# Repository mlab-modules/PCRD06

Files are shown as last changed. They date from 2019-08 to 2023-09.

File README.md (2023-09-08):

<!--- PrjInfo ---> <!--- Please remove this line after manually editing --->
<!--- 00a56be08b96043df9e37d6aff7b6990 --->
<!--- Created:2019-08-04 12:46:39.528455: --->
<!--- Author:: --->
<!--- AuthorEmail:: --->
<!--- Tags:: --->
<!--- Ust:: --->
<!--- Label --->
<!--- ELabel --->
<!--- Name:PCRD06A: --->
# PCRD06A Sample and hold circuit with analog memory
<!--- LongName --->
Signal follower with analog memory. It is a circuit equivalent to a sample-hold circuit triggered by a falling edge of signal or a circuit equivalent to a peak detector. The PCRD06A module is normally used in combination with SiPM based scintillation detector.

Examples of detectors that could be connected to the PCRD analog-backend.

  * [SIMP02](https://github.com/mlab-modules/SIPM02)
  * [USTSIPM01](https://github.com/ust-modules/USTSIPM01)

<!--- ELongName --->

<!--- Lead --->

<!--- ELead --->

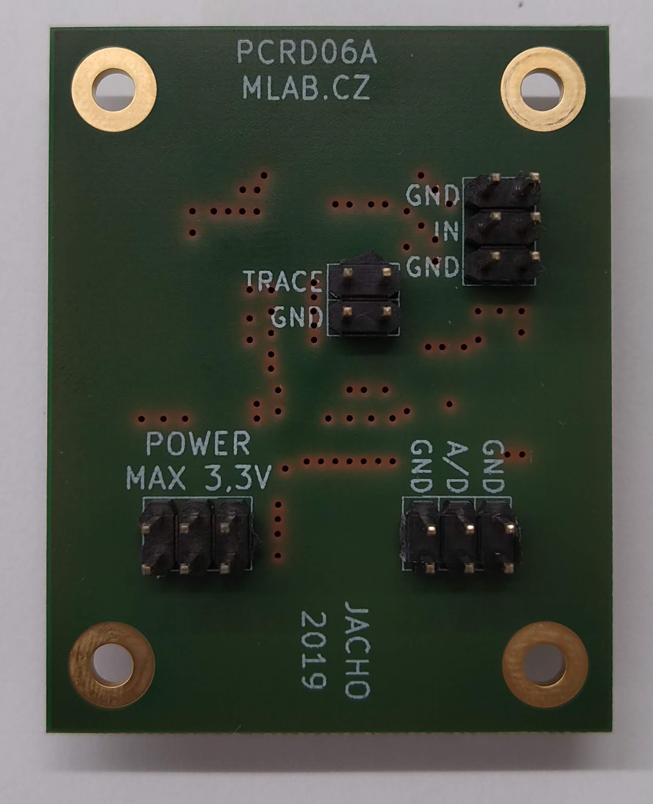
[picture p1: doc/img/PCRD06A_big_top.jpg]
PCRD06A


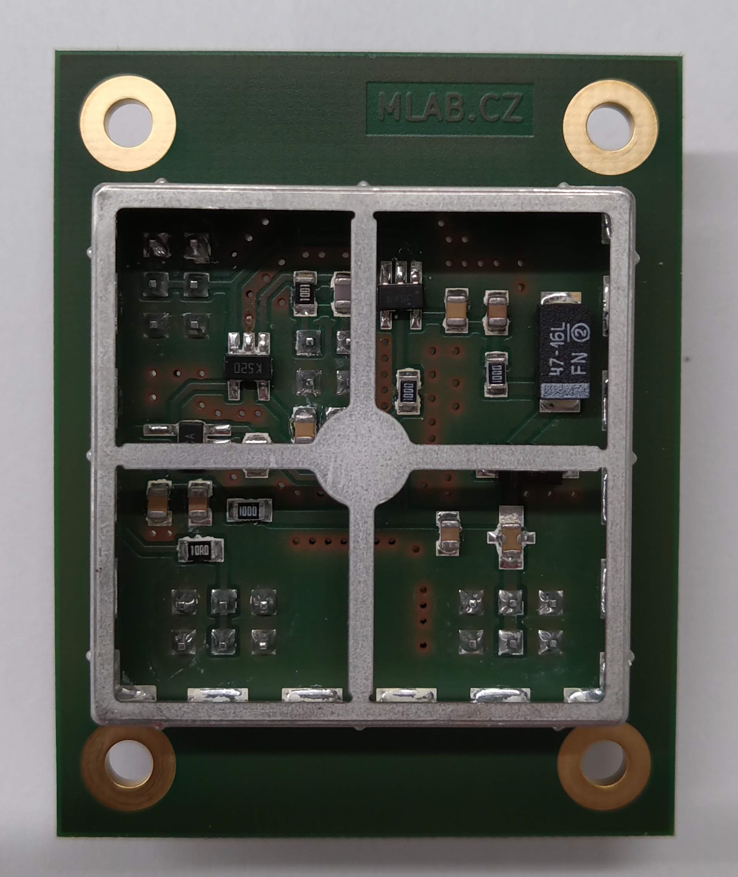
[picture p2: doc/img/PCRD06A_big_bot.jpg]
PCRD06A


<!--- Description --->

### Basic usage 

The circuit is able to operate in multiple modes. The operation mode depends on the logic used to control the circuit.  

  1. The first operation mode is the peak detector, which stores the maximal value of peak output from SiPM. This mode holds the maximal value of pulse until the circuit is reset (usually after AD conversion)
  2. Pulse discriminator, where the AD converted value is compared with a predefined threshold. After passing this threshold the circuit should be reset. 
  3. The energy integrator in that mode signal is ADconverted as fast as possible, and the dose is integrated numerically over the specified time interval. 

### Principle of function 

The signal output from the scintillation detector is a pulse. The pulses are stored in a specially developed sample-hold circuit that behaves as a signal follower and analog memory. When signal #PeakDetect_Trace is in H an analog switch U5 turns on and a signal at an output U2 follows a signal at the input with a slight delay which is done by R13 and C19. If signal #PeakDetect_Trace is switched to a high impedance state the analog switch U5 starts to be controlled by a comparator U1. In this case, when the input signal goes from high to low, a positive input of the comparator will be at a higher voltage than a negative input, following a voltage at capacitor C19.

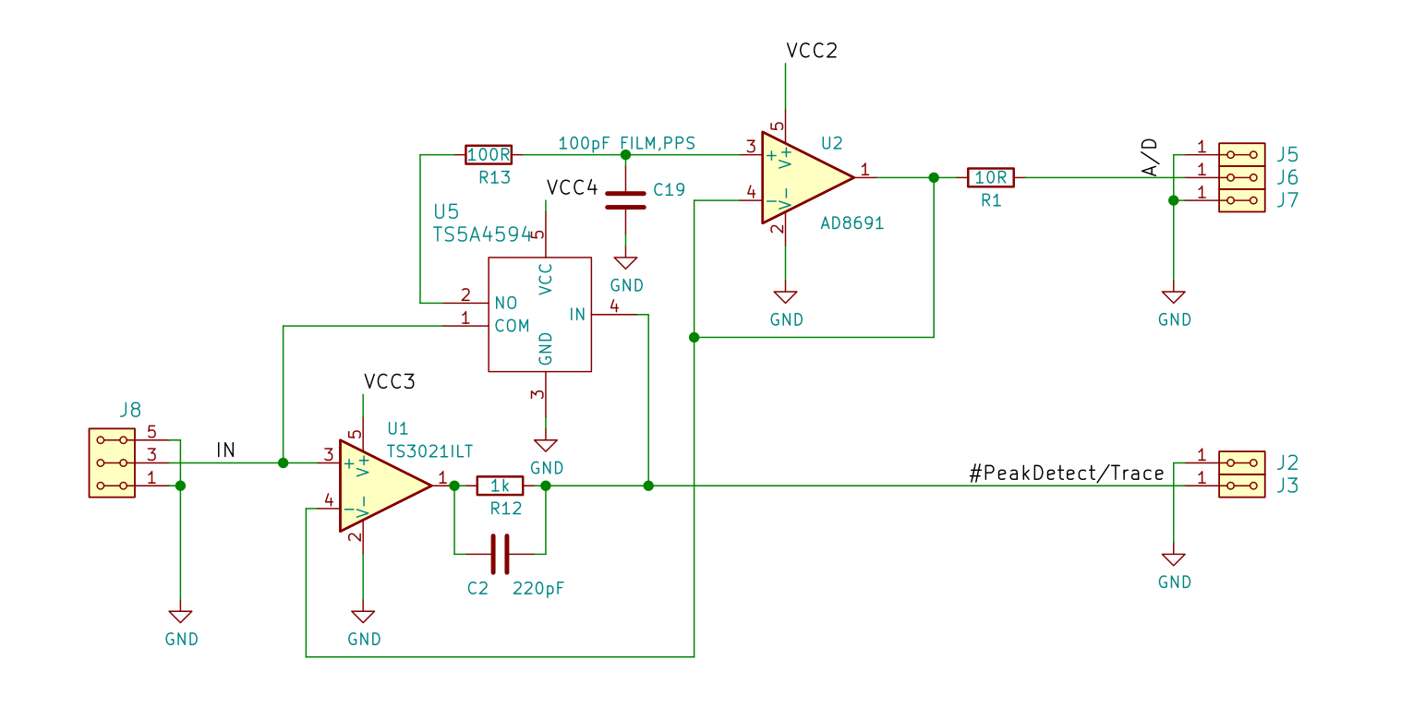
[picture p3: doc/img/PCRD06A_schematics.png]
PCRD06A


It causes the switching-off of the analog switch U5 and the capacitor C19 holds its last voltage value. This behavior is similar to a peak detector circuit. In the next step, the stored voltage can be converted by ADC connected at the output and after this conversion, the input #PeakDetect_Trace goes again to H and the circuit changes behavior to signal follower circuit. The described sample-hold circuit does not suffer from typical peak detector circuit ills like insensitivity to small signals, mistreatment of negative signals, or discharging the capacitor by leakage current through diodes.

Moreover, this circuit can be used as a pulse discriminator as well. The signal #PeakDetect_Trace can be connected to an input of digital circuits when it is controlled by the comparator U1. When the input signal goes from high to low, the signal #PeakDetect_Trace goes from high to low as well. This behavior can be used for the detection of the falling edge of the signal. There is only one constraint of this circuit, the input signal can not change raising/falling time widely and the RC time constant (R13, C19) must be chosen correctly, respecting the input signal time properties.

More details about the principle are in [DOCTORAL THESIS, Research on cosmic rays on board aircraft using a newly developed PIN diode detector, 2020, CTU in Prague](http://www.ujf.cas.cz/export/sites/ujf/.content/files/CRREAT/kakona_thesis.pdf)

<!--- EDescription --->
<!--- Content --->
<!--- EContent --->
<sub><sup> Generated with [MLABweb](https://github.com/MLAB-project/MLABweb). (2019-08-04)</sup></sub>

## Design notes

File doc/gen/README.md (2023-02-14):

# PCB

Board size: 50.29x40.13 mm (1.98x1.58 inches)

- This is the size of the rectangle that contains the board
- Thickness: 1.6 mm (63 mils)
- Material: FR4
- Finish: HAL
- Layers: 2
- Copper thickness: 35 µm

Solder mask: TOP / BOTTOM

- Color: Green

Silk screen: TOP / BOTTOM

- Color: White

# Important sizes

Clearance: 0.2 mm (8 mils)

Track width: 0.25 mm (10 mils)

- By design rules: 0.2 mm (8 mils)

Drill: 0.5 mm (20 mils)

- Vias: 0.5 mm (20 mils) [Design: 0.4 mm (16 mils)]
- Pads: 1.0 mm (39 mils)
- The above values are real drill sizes, they add 0.1 mm (4 mils) to plated holes (PTH)

Via: 0.8/0.4 mm (31/16 mils)

- By design rules: 0.8/0.3 mm (31/12 mils)
- Micro via: no [0.2/0.1 mm (8/4 mils)]
- Burried/blind via: no

Outer Annular Ring: 0.15 mm (6 mils)

- By design rules: 0.15 mm (6 mils)

Eurocircuits class: 4B
- Using min drill 0.5 mm for an OAR of 0.15 mm

# General stats

Components count: (SMD/THT)

- Top: 0/11 (THT)
- Bottom: 21/1 (SMD + THT)

Defined tracks:

- 0.25 mm (10 mils)
- 0.3 mm (12 mils)
- 0.4 mm (16 mils)
- 0.5 mm (20 mils)
- 0.6 mm (24 mils)
- 0.7 mm (28 mils)
- 0.8 mm (31 mils)

Used tracks:

- 0.25 mm (10 mils) (6) defined: yes
- 0.4 mm (16 mils) (68) defined: yes
- 0.8 mm (31 mils) (17) defined: yes

Defined vias:

- 0.8/0.4 mm (31/16 mils)

Used vias:

- 0.8/0.4 mm (31/16 mils) (Count: 72, Aspect: 2.0 A) defined: yes

Holes (excluding vias):

- 0.89 mm (35 mils) (22)
- 3.0 mm (118 mils) (4)

Oval holes:

Drill tools (including vias and computing adjusts and rounding):

- 0.5 mm (20 mils) (72)
- 1.0 mm (39 mils) (22)
- 3.1 mm (122 mils) (4)

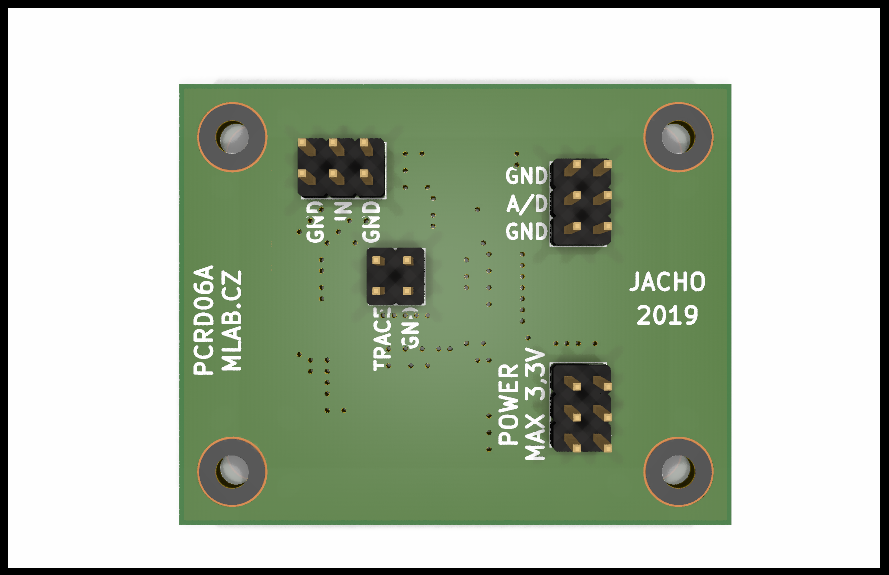
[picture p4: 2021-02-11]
doc/img/PCRD06A_PC_big_top.png

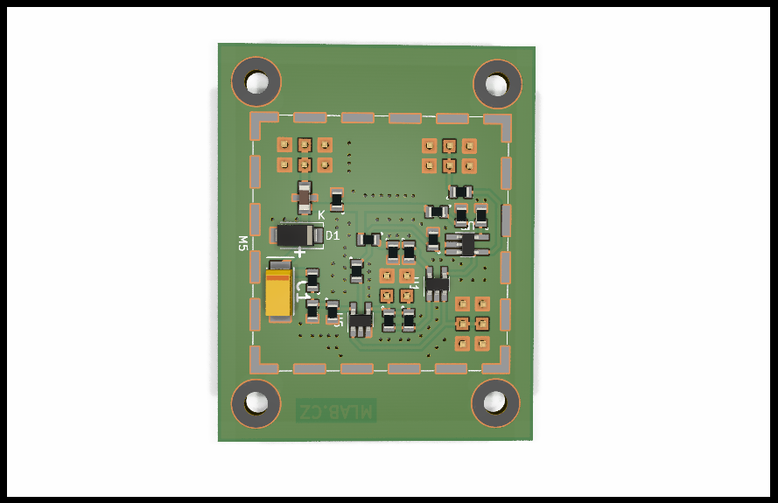
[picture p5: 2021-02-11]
doc/img/PCRD06A_PC_big_bot.png

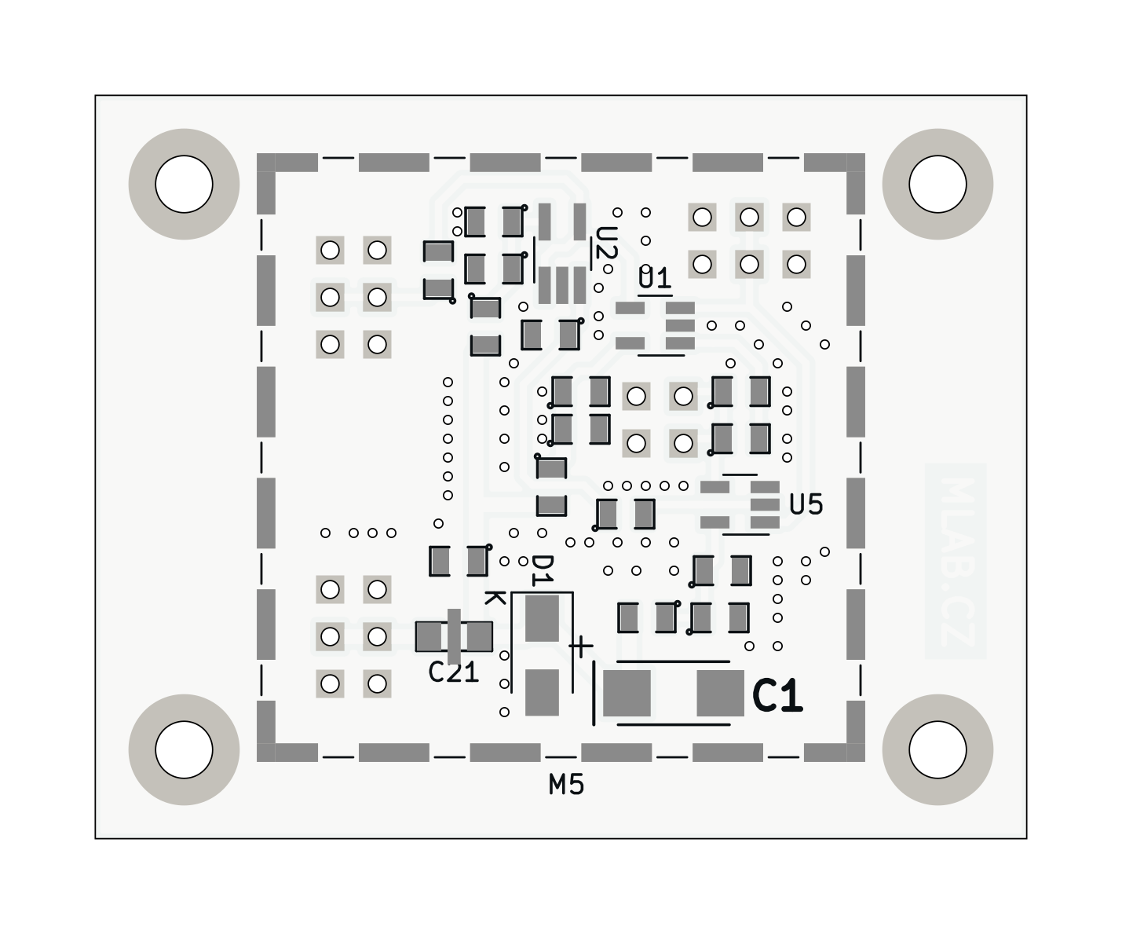
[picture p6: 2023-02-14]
doc/gen/img/PCRD06A-bottom.png

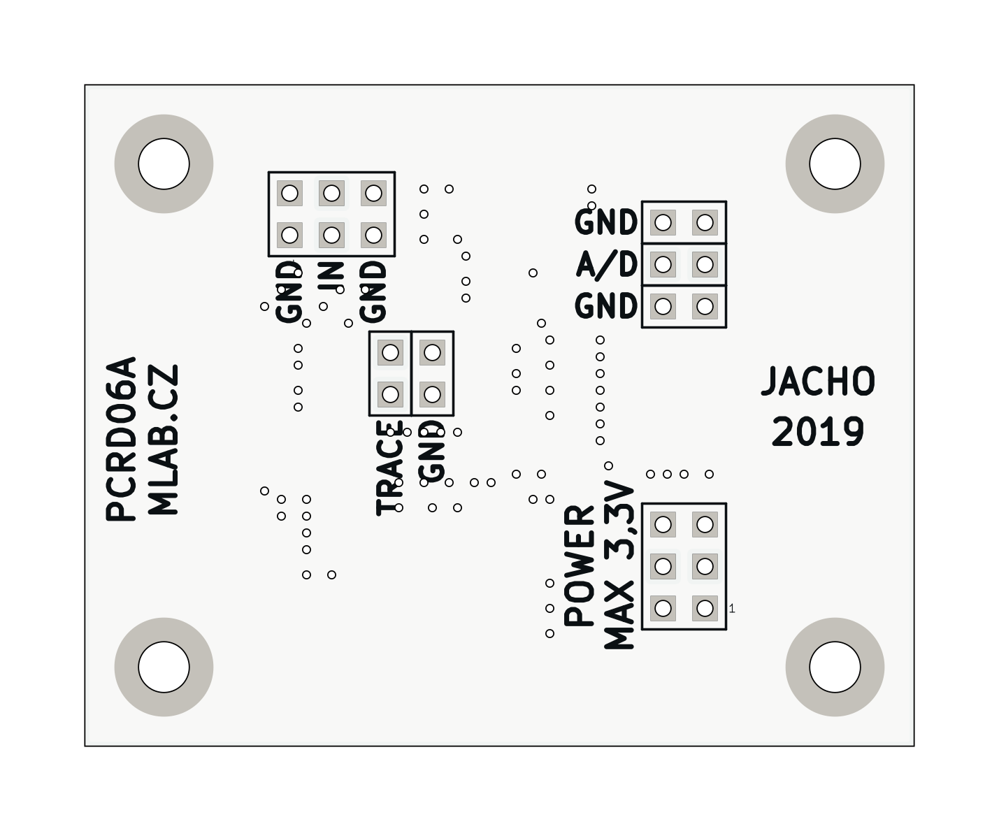
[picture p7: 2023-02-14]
doc/gen/img/PCRD06A-top.png

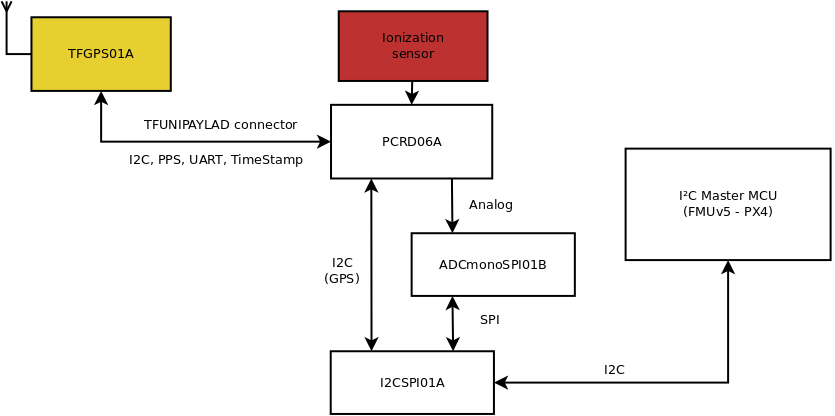
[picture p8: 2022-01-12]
doc/img/Proposed_improvement.png

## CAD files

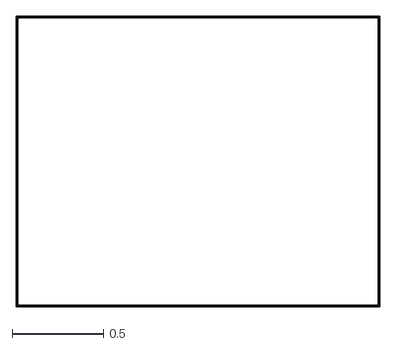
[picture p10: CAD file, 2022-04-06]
doc/gen/dxf/PCRD06A-Edge_Cuts.dxf
1.99 x 1.59

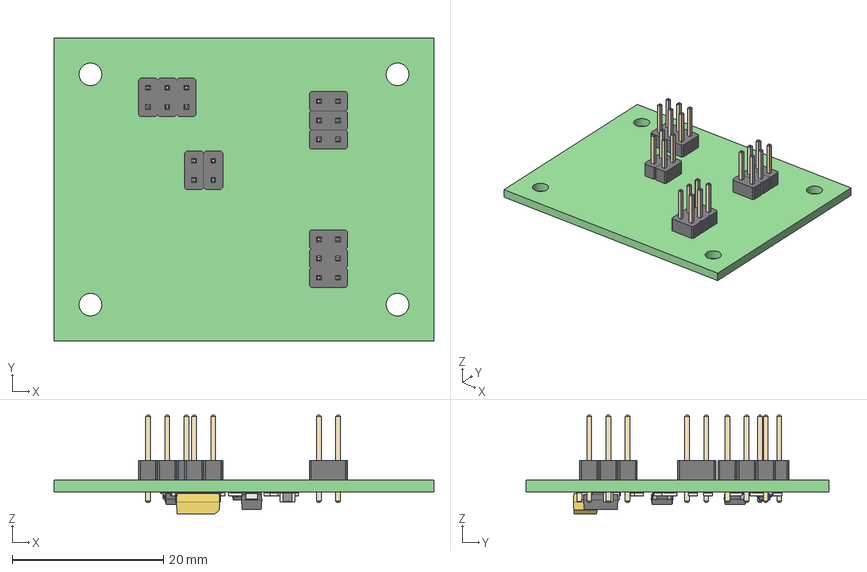
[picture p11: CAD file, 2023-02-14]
doc/gen/PCRD06A.step
50.3 x 40.1 x 13.0 mm
tmpduxnie4c PCB

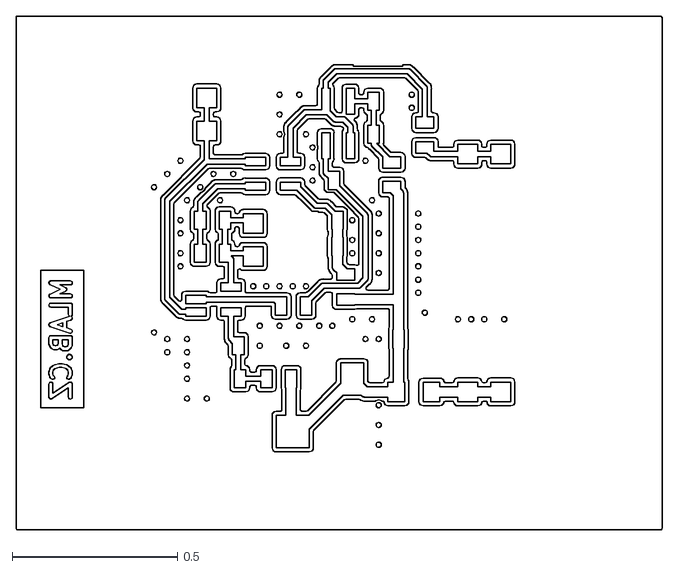
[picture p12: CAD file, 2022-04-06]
doc/gen/dxf/PCRD06A-B_Cu.dxf
1.96 x 1.56

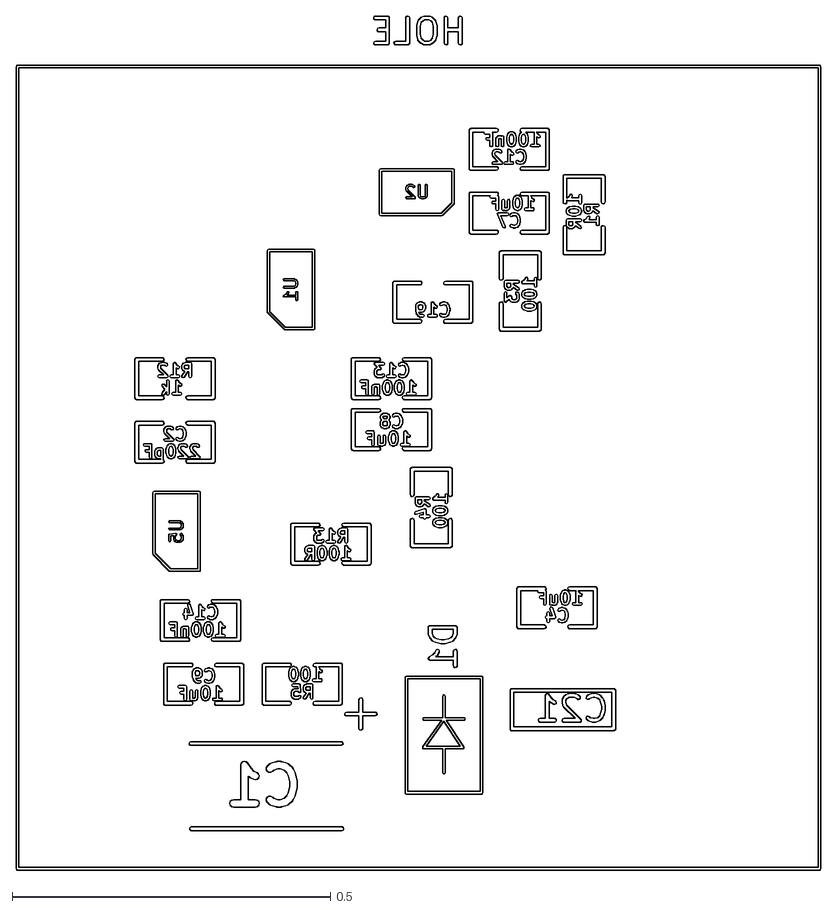
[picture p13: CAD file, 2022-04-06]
doc/gen/dxf/PCRD06A-B_Fab.dxf
1.26 x 1.34

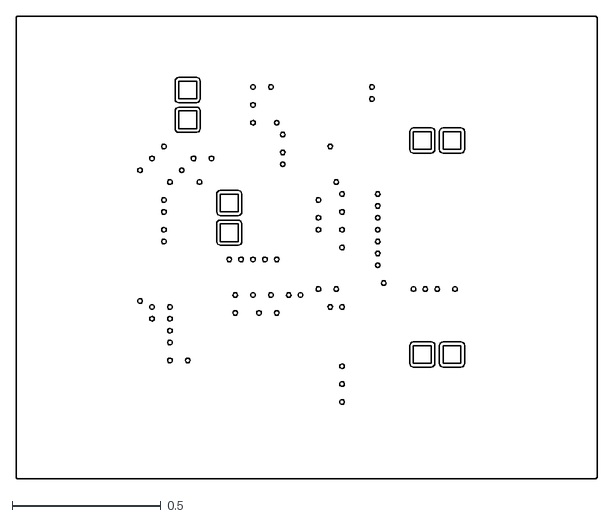
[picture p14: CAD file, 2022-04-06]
doc/gen/dxf/PCRD06A-F_Cu.dxf
1.96 x 1.56

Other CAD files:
doc/gen/dxf/PCRD06A-F_Fab.dxf
doc/gen/dxf/PCRD06A-B_Mask.dxf
doc/gen/dxf/PCRD06A-B_Paste.dxf
doc/gen/dxf/PCRD06A-B_Silkscreen.dxf
doc/gen/dxf/PCRD06A-F_Mask.dxf
doc/gen/dxf/PCRD06A-F_Silkscreen.dxf

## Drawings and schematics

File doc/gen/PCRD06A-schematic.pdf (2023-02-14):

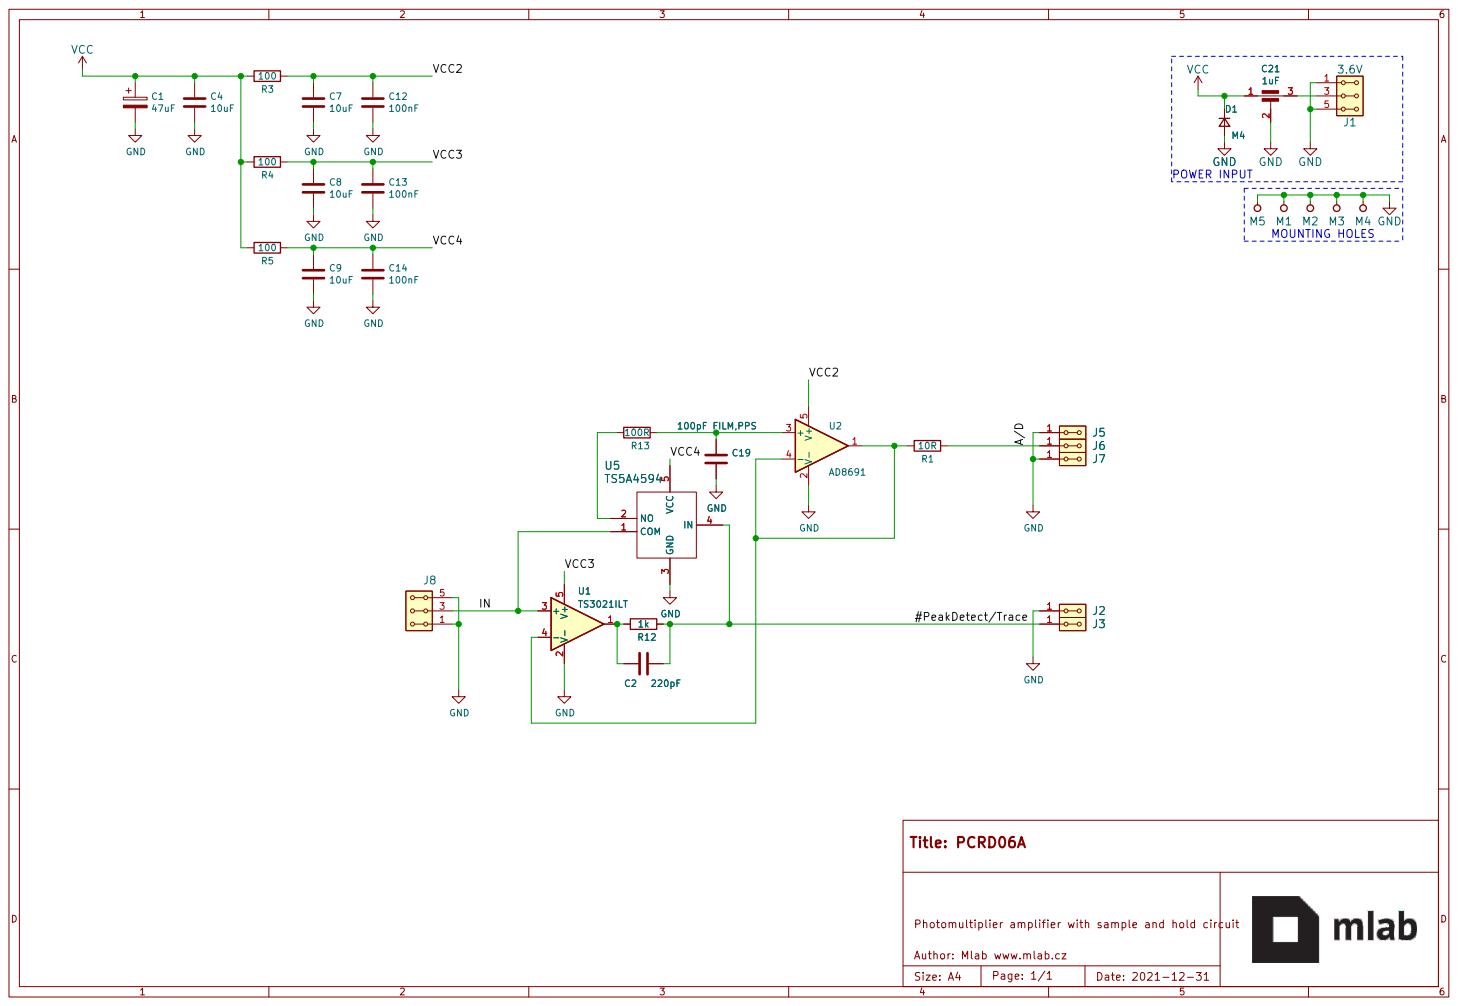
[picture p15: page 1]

Photomultiplier amplifier with sample and hold circuit

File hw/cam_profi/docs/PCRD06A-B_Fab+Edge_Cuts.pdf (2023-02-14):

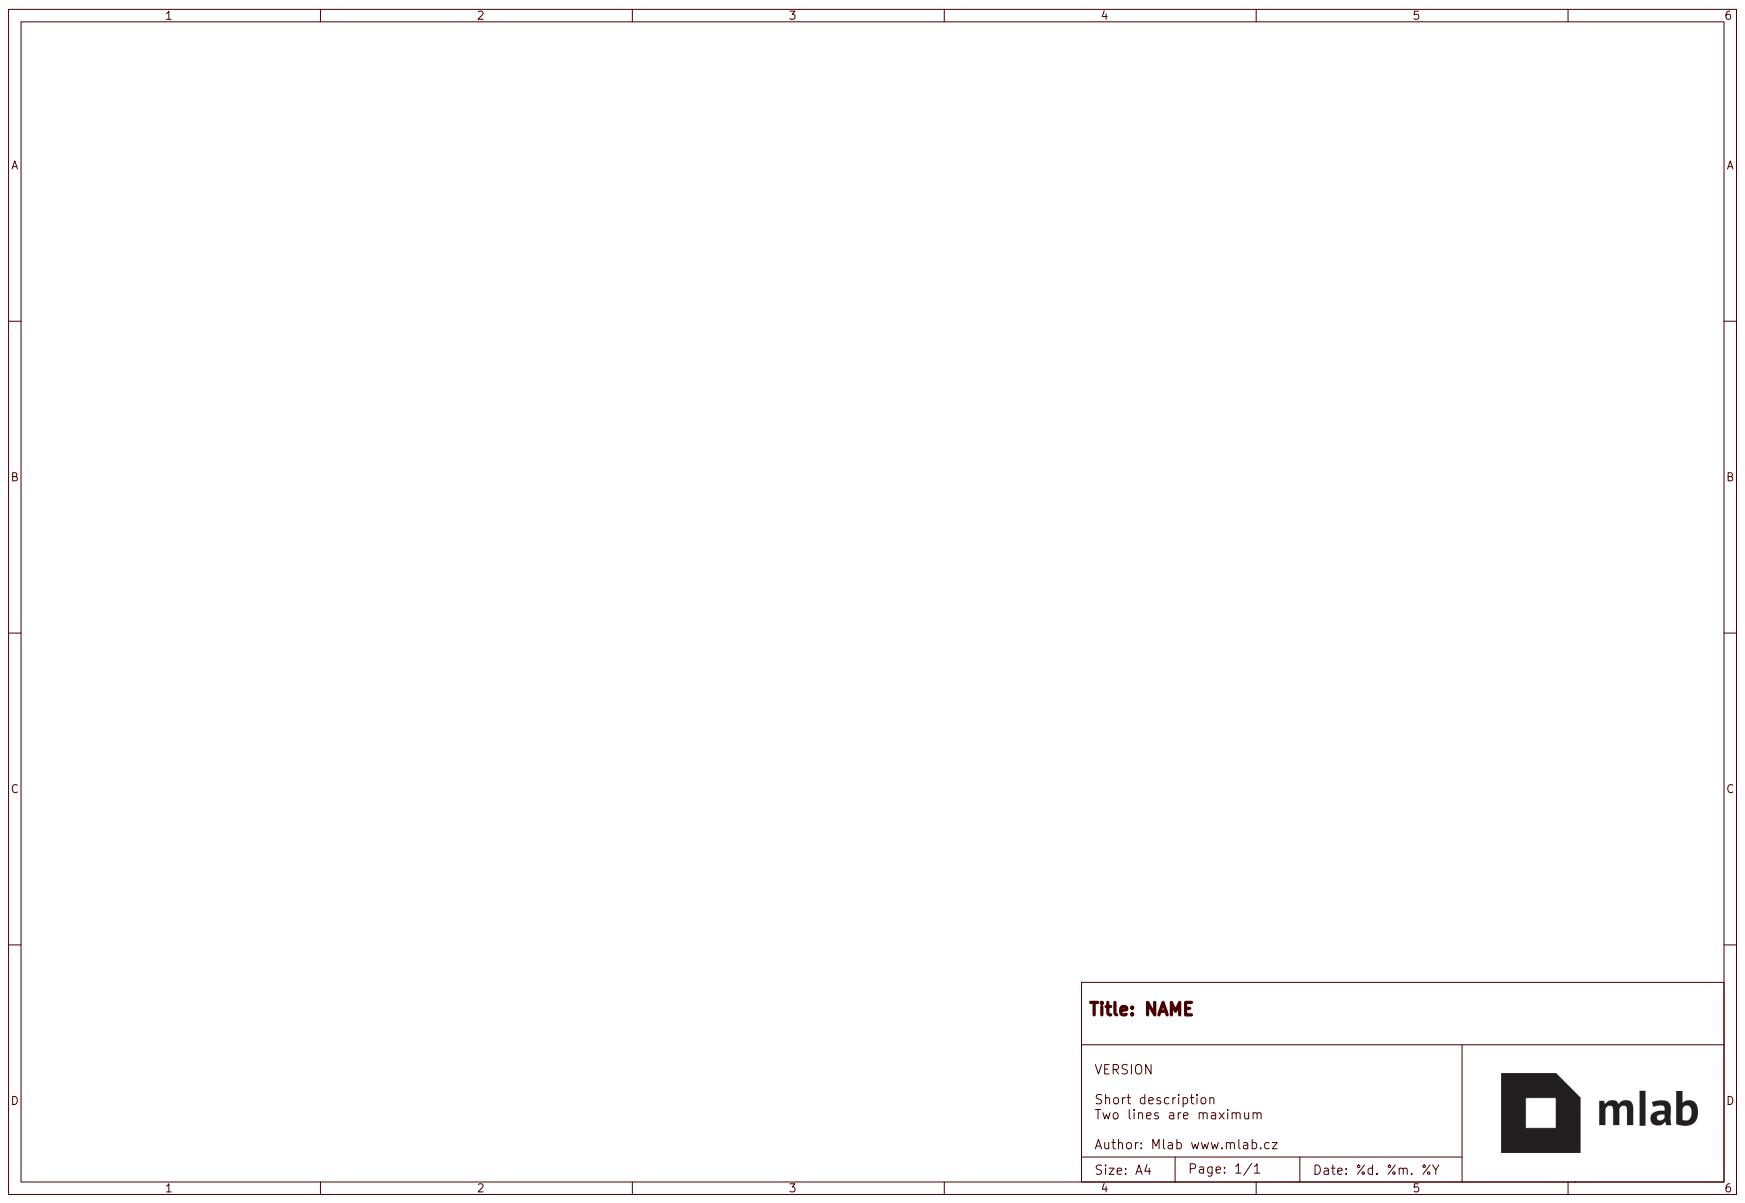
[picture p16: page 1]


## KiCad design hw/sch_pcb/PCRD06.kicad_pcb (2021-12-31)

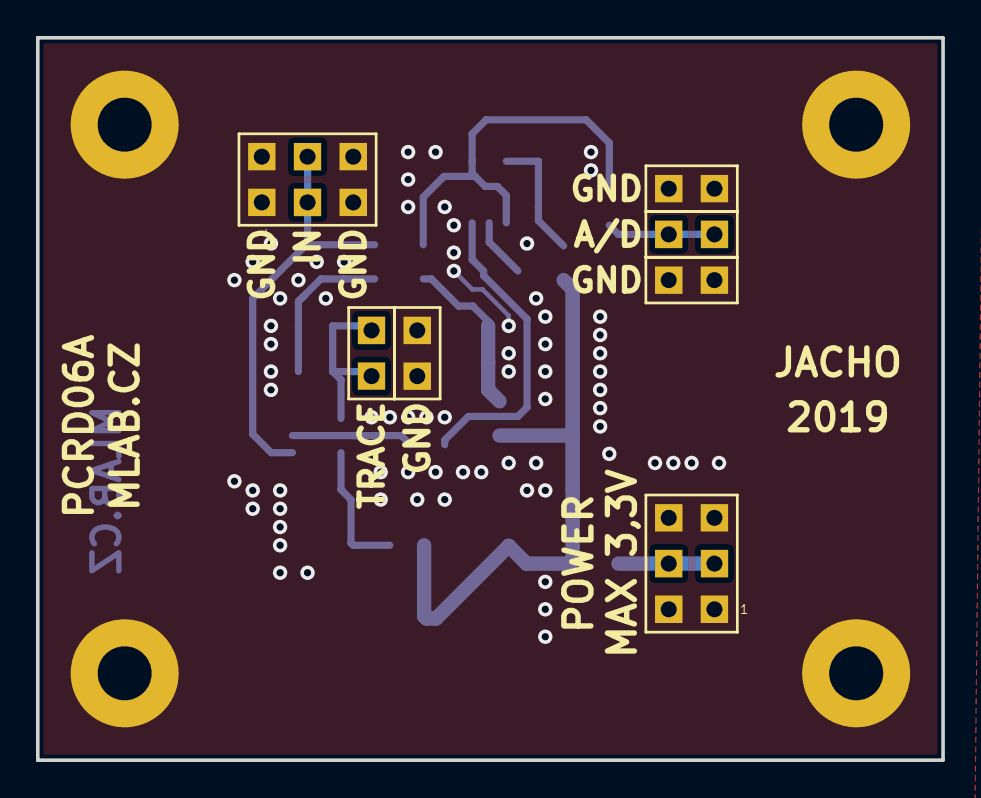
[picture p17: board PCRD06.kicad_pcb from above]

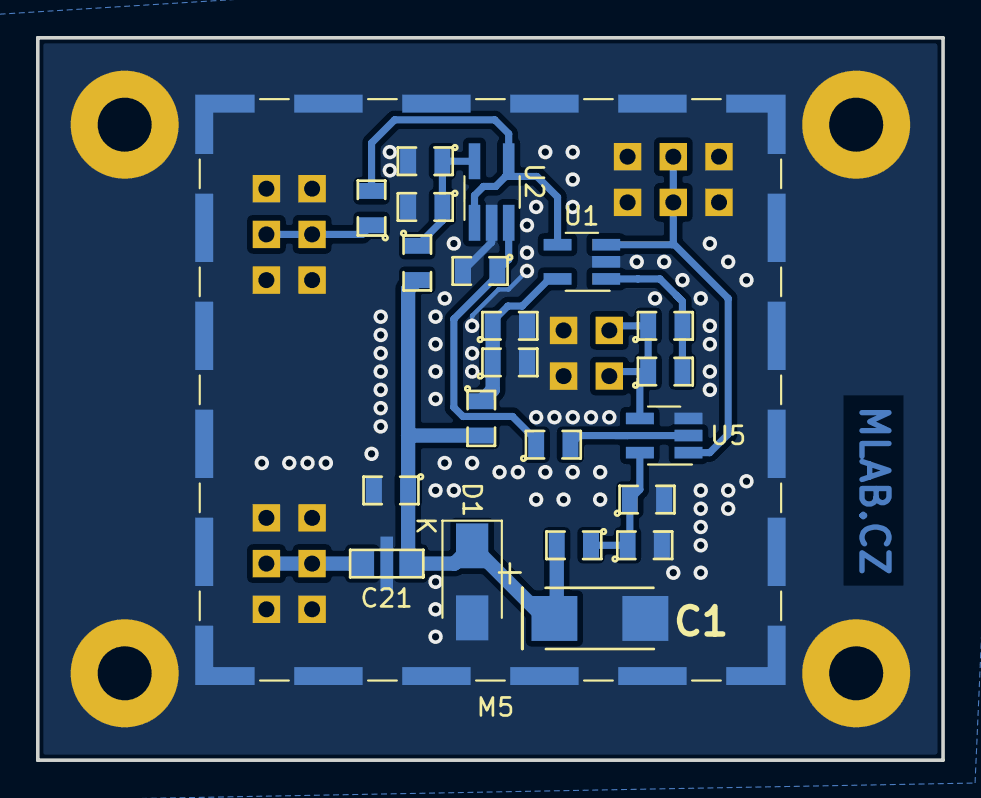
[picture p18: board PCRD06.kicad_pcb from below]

Board: 2 copper layers, 50.3 x 40.1 mm, 33 parts (22 on the bottom side), 13 nets.

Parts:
C1: 47uF; TantalC_SizeC_Reflow
C2: 220pF; SMD-0805
C4, C7, C8, C9: 10uF; SMD-0805
C12, C13, C14: 100nF; SMD-0805
C19: 100pF FILM,PPS; SMD-0805
C21: 1uF; FIR_0805
D1: M4; Diode-SMA_Standard
J1: 3.6V; Straight_2x03
J2, J3, J5, J6, J7: HEADER_2x01_PARALLEL; Straight_2x01
J8: HEADER_2x03_PARALLEL; Straight_2x03
M1, M2, M3, M4: HOLE; MountingHole_3mm
M5: HOLE; Laird_Technologies_BMI-S-204-F_32.00x32.00mm
R1: 10R; SMD-0805
R3, R4, R5: 100; SMD-0805
R12: 1k; SMD-0805
R13: 100R; SMD-0805
U1: TS3021ILT; SOT-23-5_HandSoldering
U2: AD8691; TSOT-23-5_HandSoldering
U5: TS5A4594; SOT-23-5_HandSoldering

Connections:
/#PeakDetect/Trace: C2.1, J3.1, J3.2, R12.1, U5.4
/A/D: J6.1, J6.2, R1.1
/IN: J8.3, J8.4, U1.3, U5.1
/VCC2: C7.1, C12.1, R3.1, U2.5
/VCC3: C8.1, C13.1, R4.1, U1.5
/VCC4: C9.1, C14.1, R5.1, U5.5
GND: C1.2, C4.2, C7.2, C8.2, C9.2, C12.2, C13.2, C14.2, C19.2, C21.2, D1.2, J1.1, J1.2, J1.5, J1.6, J2.1, J2.2, J5.1, J5.2, J7.1, J7.2, J8.1, J8.2, J8.5, J8.6, M1.1, M2.1, M3.1, M4.1, M5.1, U1.2, U2.2, U5.3
unnamed: C2.2, R12.2, U1.1
unnamed: C19.1, R13.1, U2.3
unnamed: C21.3, J1.3, J1.4
unnamed: R1.2, U1.4, U2.1, U2.4
unnamed: R13.2, U5.2
VCC: C1.1, C4.1, C21.1, D1.1, R3.2, R4.2, R5.2

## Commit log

2019-08-04 [MLABweb] Documentation edits; PCRD06A
    [PCRD06A.kicad_pcb, PCRD06A.sch]
2019-08-05 Edit PCB
    [PCRD06A.kicad_pcb, PCRD06A.sch]
2019-08-06 Generovani vyrobnich dat
    [PCRD06A-B_Cu.gbr, PCRD06A-B_Mask.gbr, PCRD06A-Edge_Cuts.gbr, PCRD06A-F_Cu.gbr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]
2021-02-11 Přegenerování výrobních dat.
    [PCRD06A-B.Cu.gbr, PCRD06A-B.Mask.gbr, PCRD06A-B_Cu.gbr, PCRD06A-B_Mask.gbr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]
2021-12-31 Update documentation.
    [PCRD06A.kicad_pcb, PCRD06A.kicad_sch, PCRD06A.sch]
2022-04-06 Update actions products
    [PCRD06A-B_Cu.dxf, PCRD06A-B_Cu.gbr, PCRD06A-B_Fab.dxf, PCRD06A-B_Mask.dxf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]
2023-07-05 automated commit; rename source files to new naming convence
    [PCRD06.kicad_pcb, PCRD06.kicad_sch]
2023-09-09 Add links to datasheets.
    [PCRD06.kicad_sch]
